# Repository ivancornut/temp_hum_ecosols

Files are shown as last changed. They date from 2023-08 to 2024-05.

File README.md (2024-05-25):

# Accurate microclimate measures
The aim of this project is to build an accurate air temperature and humidity sensor for environmental science. We will be using the SHT45 sensor from sensirion since it presents the right accuracy, precicison and drift for the job. Due to its use outdoors we will use the version equipped with a PTFE filter membrane. 

## Hardware

### Electronics
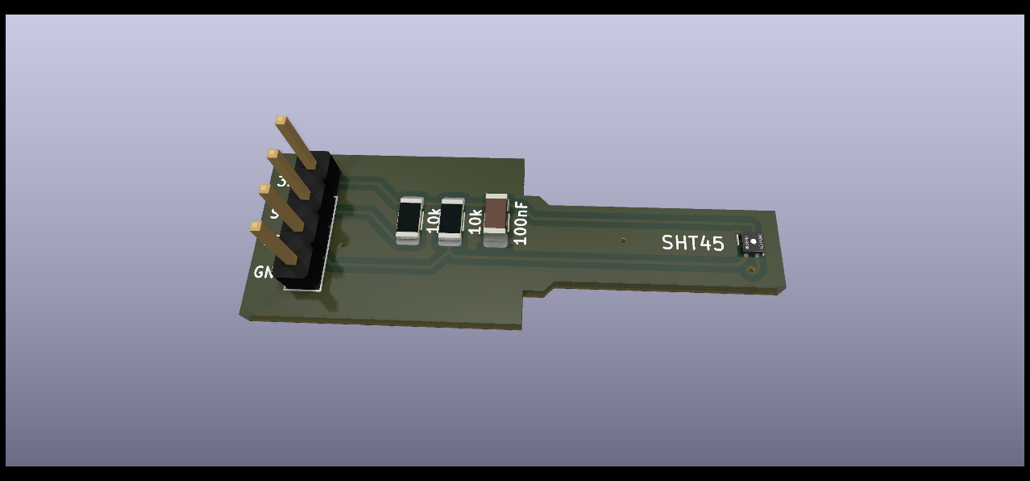
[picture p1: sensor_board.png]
SHT45 board

#### Bill of materials
- 2 10kOhm 1206 resistors (0.109€ - bought [here](https://fr.rs-online.com/web/p/resistances-a-montage-en-surface/6791765))
- 1 100nF 1206 capacitor (0.05€ - bought [here](https://fr.rs-online.com/web/p/condensateurs-ceramique-multicouches/1335654))
- 1 SHT45-AD1F-R2 sensirion sensor (3.07 € - bought [here](https://www.mouser.fr/ProductDetail/403-SHT45-AD1F-R2))
- 50 PCBs and 1 stencil (70€ - PCBway)

#### Cost per sensor
The cost of the sensor board is 5€. Time to apply solder paste and reflow is around 20min. So considering somebody paid 60€ an hour this amounts to 25€ per sensor. 

### Microclimate radiation shield
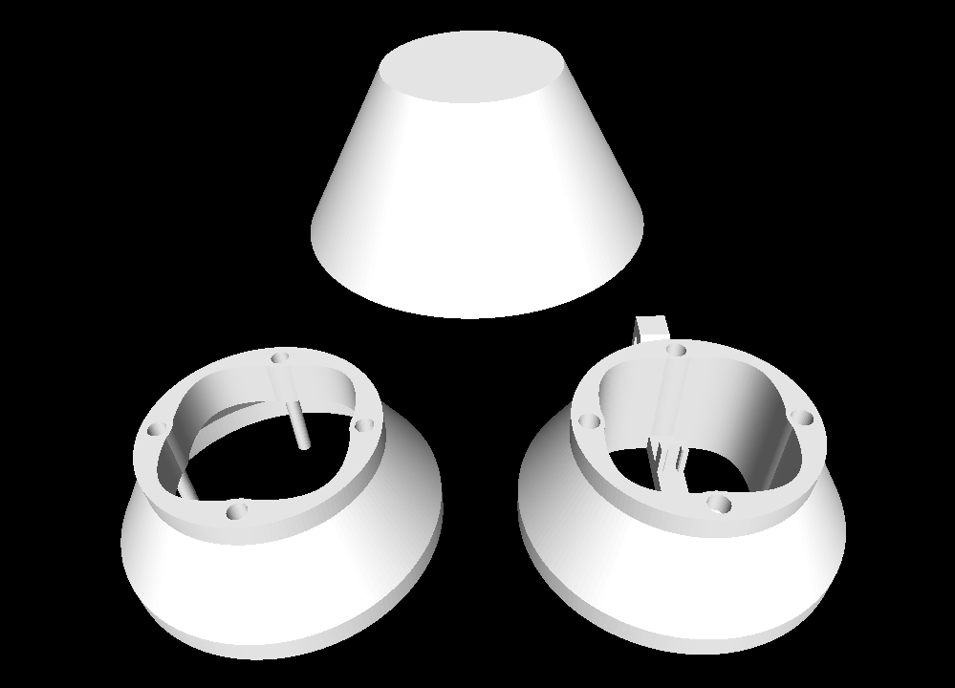
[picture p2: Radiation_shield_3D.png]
Radiation shield

#### Design
To complement the sensor we have designed a small and discrete radiation shield that is optimised for 3D printing. This is to be used inside canopies to measure the local microclimate. It is designed in 3 parts and the bottom part has a well-adjuster holder for the PCB.
This piece should ideally be printed with UV resistant white PETG. We use the Nanovia PETG-GF-UV: [https://nanovia.tech/en/ref/nanovia-petg-gf-uv/](https://nanovia.tech/en/ref/nanovia-petg-gf-uv/)

#### Cost per shield
The material costs per shield are estimated at around 3€ if we consider that a 500g spool of this filament costs around 40€. 

## Final result

### Shield
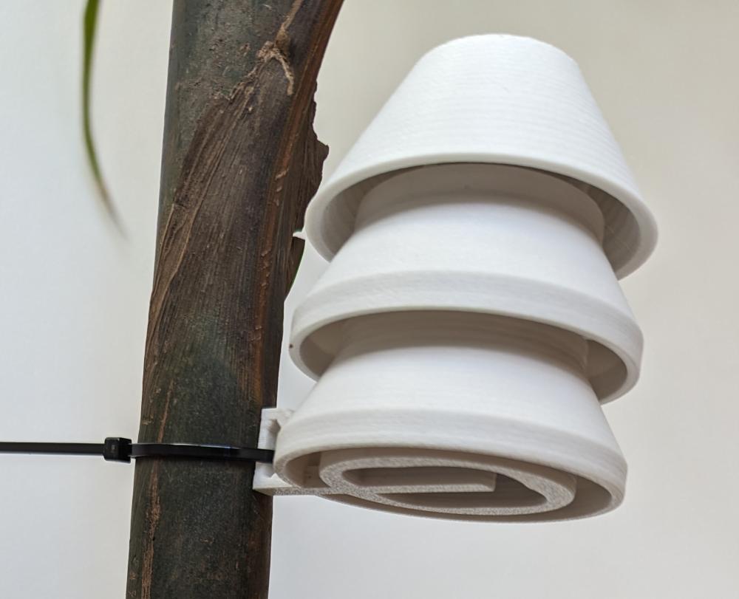
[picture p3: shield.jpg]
shield


### Front of the reflowed board
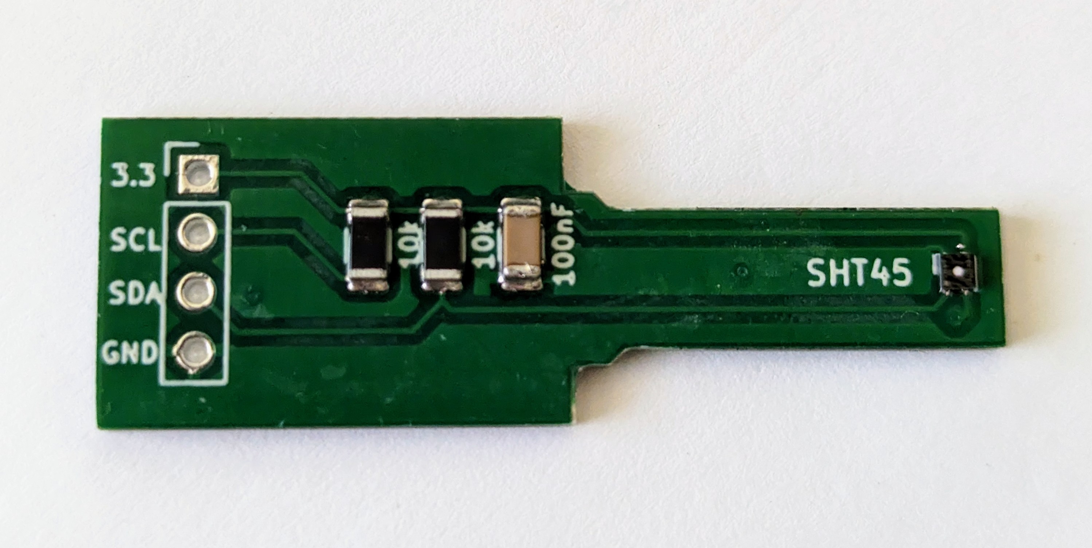
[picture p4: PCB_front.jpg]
Front of the board


### Back of the reflowed board
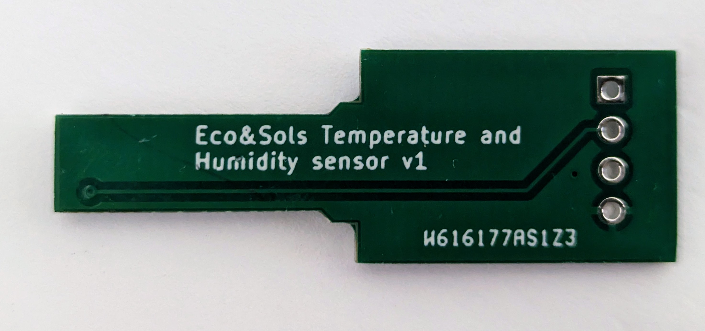
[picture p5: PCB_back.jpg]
Back of the board


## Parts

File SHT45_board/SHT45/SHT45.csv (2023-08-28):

# | Reference | Qty | Value | Footprint | DNP
1 | C1 | 1 | 100nF | Capacitor_SMD:C_1206_3216Metric
2 | J1 | 1 | Conn_01x04_Socket | Connector_PinHeader_2.54mm:PinHeader_1x04_P2.54mm_Vertical
3 | R1, R2 | 2 | 10k | Resistor_SMD:R_1206_3216Metric
4 | U1 | 1 | SHT4x | Sensor_Humidity:Sensirion_DFN-4_1.5x1.5mm_P0.8mm_SHT4x_NoCentralPad

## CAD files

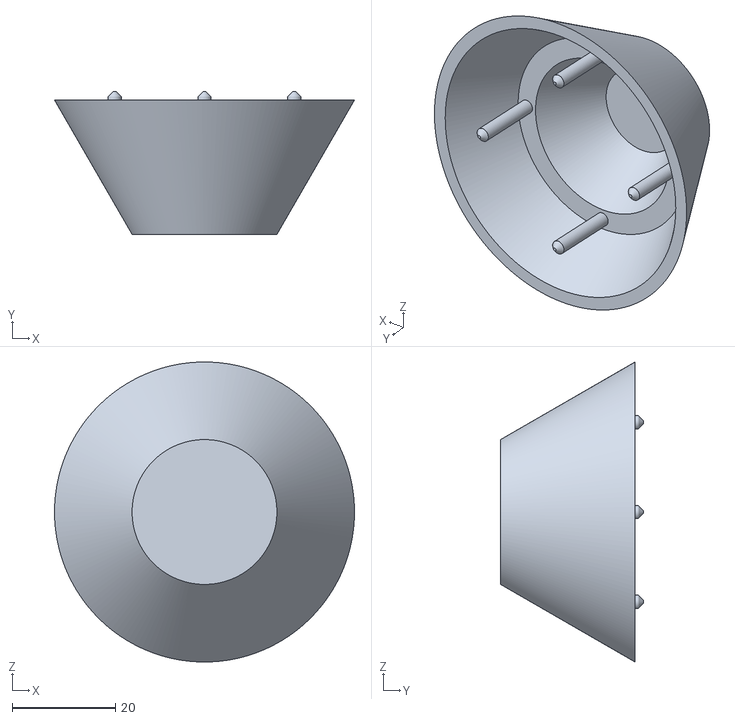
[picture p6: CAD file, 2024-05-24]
top_element.stl
58.0 x 27.6 x 58.0

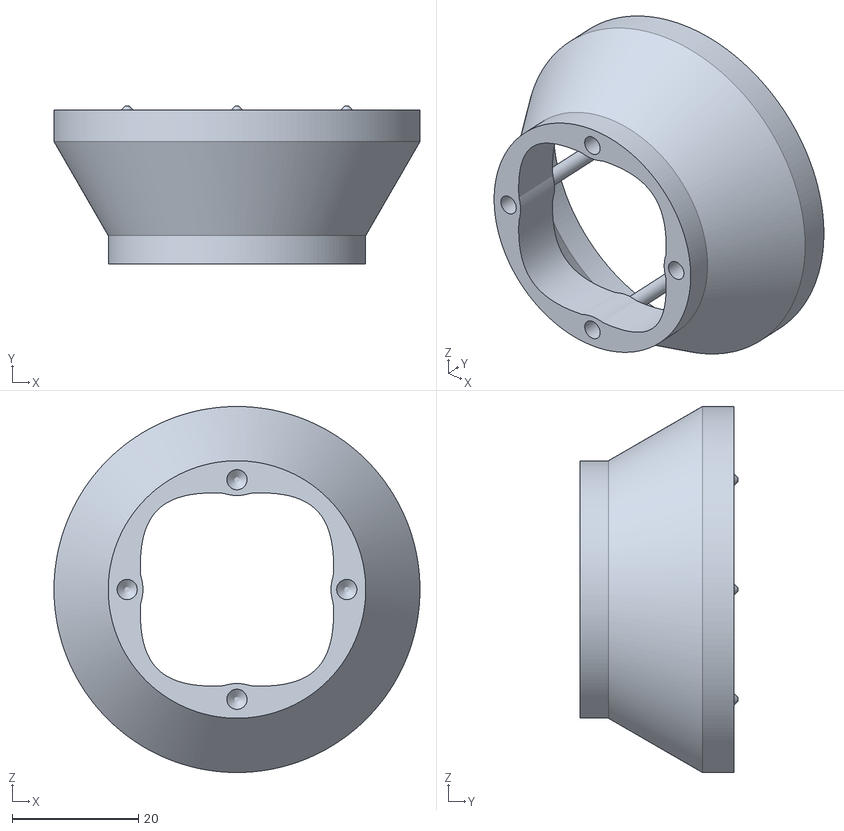
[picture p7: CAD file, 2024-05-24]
standard_element.stl
58.0 x 25.0 x 58.0

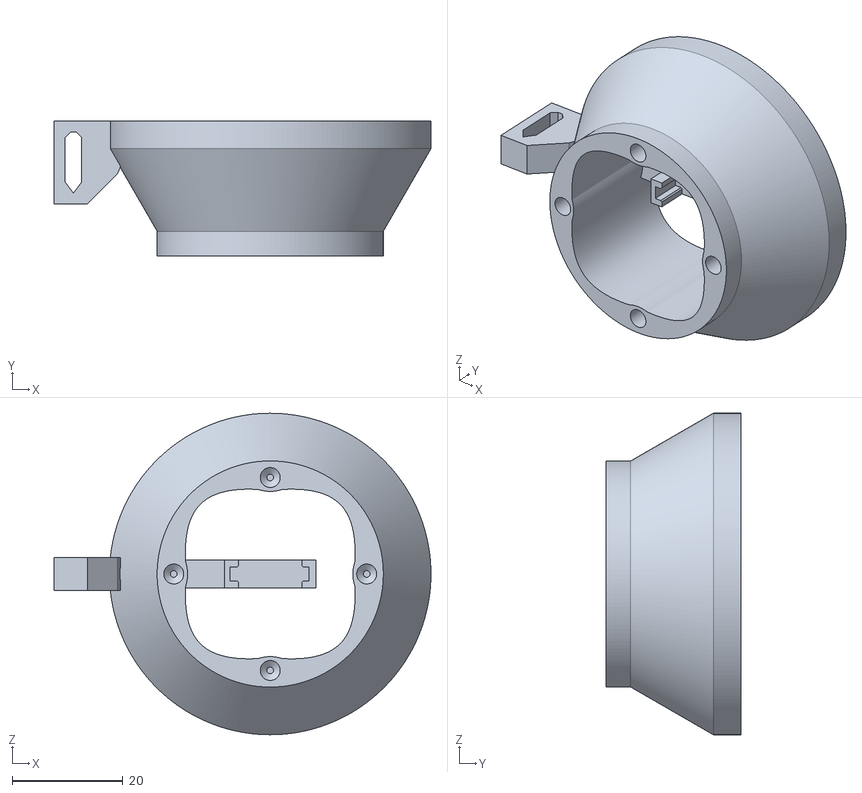
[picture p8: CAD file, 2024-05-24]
Bottom_element.stl
68.0 x 24.4 x 58.0

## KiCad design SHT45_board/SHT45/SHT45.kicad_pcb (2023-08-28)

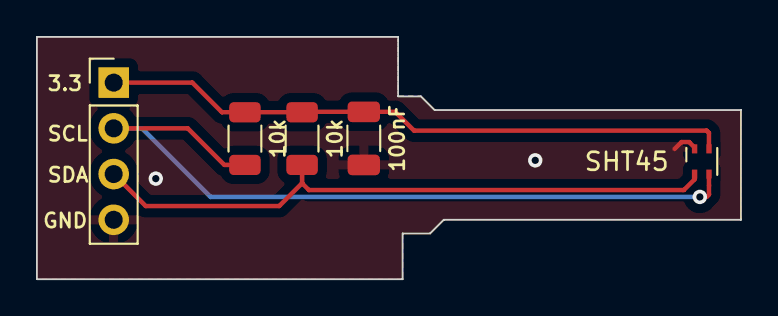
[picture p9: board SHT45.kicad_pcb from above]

Board: 2 copper layers, 39.1 x 13.5 mm, 5 parts (0 on the bottom side), 4 nets.

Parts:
10k, 10k#2: 10k; R_1206_3216Metric
100nF: 100nF; C_1206_3216Metric
J1: Conn_01x04_Socket; PinHeader_1x04_P2.54mm_Vertical
SHT45: SHT4x; Sensirion_DFN-4_1.5x1.5mm_P0.8mm_SHT4x_NoCentralPad

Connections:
+3.3V: 10k.1, 10k#2.1, 100nF.1, J1.1, SHT45.3 (VDD)
/SCL: 10k.2, J1.2, SHT45.2 (SCL)
/SDA: 10k#2.2, J1.3, SHT45.1 (SDA)
GND: 100nF.2, J1.4, SHT45.4 (VSS)

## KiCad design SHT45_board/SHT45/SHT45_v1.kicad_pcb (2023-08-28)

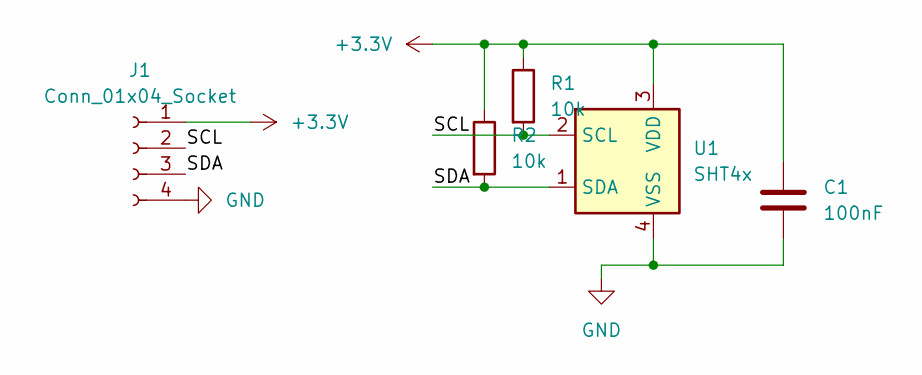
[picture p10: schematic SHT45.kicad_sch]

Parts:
C1: 100nF; C_1206_3216Metric
J1: Conn_01x04_Socket; PinHeader_1x04_P2.54mm_Vertical
R1, R2: 10k; R_1206_3216Metric
U1: SHT4x; Sensirion_DFN-4_1.5x1.5mm_P0.8mm_SHT4x_NoCentralPad

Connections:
+3.3V: C1.1, J1.1, R1.1, R2.1, U1.3 (VDD)
/SCL: J1.2, R1.2, U1.2 (SCL)
/SDA: J1.3, R2.2, U1.1 (SDA)
GND: C1.2, J1.4, U1.4 (VSS)

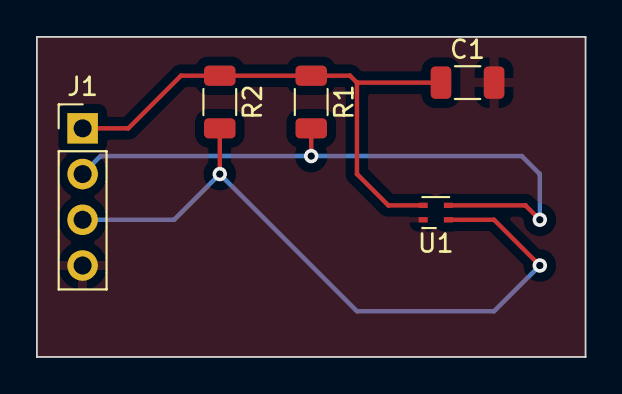
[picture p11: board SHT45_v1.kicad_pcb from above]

Board: 2 copper layers, 30.5 x 17.8 mm, 5 parts (0 on the bottom side), 4 nets.

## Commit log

2023-08-28 Creation of the repository
    [SHT45-AD1F-R2--3DModel-STEP-369182.STEP, SHT45-B_Cu.gbr, SHT45-B_Mask.gbr, SHT45-B_Paste.gbr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]
2023-08-28 Sensor board image
2023-08-30 PCB imgage
2024-05-21 Added stls for radiation shroud
    [Bottom_element.stl, standard_element.stl, top_element.stl]
2024-05-24 Update of Stls
    [Bottom_element.stl, standard_element.stl, top_element.stl]
